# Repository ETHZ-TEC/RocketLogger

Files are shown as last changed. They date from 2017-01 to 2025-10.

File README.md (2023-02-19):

# RocketLogger

The RocketLogger is a mixed-signal data logger designed for measuring and validating energy
harvesting based devices. It features the portability required for measurements in the field,
accurate voltage and current measurements with a very high dynamic range, and simultaneously
sampled digital inputs to track the state of the measured device.

## Getting Started

To install a new RocketLogger system or the Python Support Library for measurement post processing,
refer to the [Installation](#installation) section. The latest RocketLogger releases are available
from <https://github.com/ETHZ-TEC/RocketLogger/releases>.

If you want to learn more about the details of the RocketLogger, head to the [Documentation](#documentation) section.

## Project Structure

The RocketLogger project consists of three parts:
* [RocketLogger Cape](hardware), an analog current and voltage measurement front-end designed as
  an extension board, a so-called *Cape*, for the [BeagleBone Green](https://beagleboard.org/green/),
* [RocketLogger Software Stack](software) that provides all management functionality for data
  logging, including low level C API, a command line utility, and an easy-to-use web interface,
* [RocketLogger Scripts](script) to import and process RocketLogger Data
  (RLD) files and to generate the calibration data files.

## Installation

The [RocketLogger releases](https://github.com/ETHZ-TEC/RocketLogger/releases) are accompanied by
a pre-built RocketLogger flasher image that allows installation of ready-to-use software on a
RocketLogger device:

1. Flash the RocketLogger flasher image `rocketlogger-flasher-vX.X.X.img.xz` (where `X.X.X` is the targeted release) onto an SD card
   using the `software/system/flash_image.sh` script.
2. Insert the SD card into the RocketLogger and wait for the installation to complete and the
   RocketLogger to power off.
3. Remove the SD card, power on the RocketLogger again, and start your first measurements.

For more details on the installation process and alterative deployment options, refer to the [RocketLogger Installation](https://github.com/ETHZ-TEC/RocketLogger/wiki/software) wiki page.

The Python support library is available from the [Python Package Index](https://pypi.org) and
is installed using pip:
```bash
python -m pip install rocketlogger
```

For the manual installation of individual software components, see the respective README files:
* [RocketLogger software](software/rocketlogger/README.md#installation)
* [Node.js web interface](software/node_server/README.md#installation)
* [Base operating system](software/system/README.md#installation)
* [Python support library](script/python/README.md#installation)

## Documentation

The documentation for the RocketLogger is found in the wiki pages at
<https://github.com/ETHZ-TEC/RocketLogger/wiki>.

## Versioning

The RocketLogger project uses [semantic versioning](https://semver.org) for its releases.

## Dependencies

### Hardware Design

The hardware was designed using Altium Designer (version 16.1 was used for the PCB design).

More details regarding the hardware design can be found in the wiki at
[RocketLogger Hardware Design Data](https://github.com/ETHZ-TEC/RocketLogger/wiki/design-data).

### Software Stack

The RocketLogger software is based on the [Debian](https://www.debian.org) operating system for
the BeagleBone platform provided by [BeagleBoard.org](https://beagleboard.org).

To compile the RocketLogger software, the following system components are required (to be installed
using `apt-get`):

```bash
curl device-tree-compiler gcc g++ git make meson/buster-backports ninja-build/buster-backports ntp pkg-config ti-pru-cgt-installer libgpiod-dev libi2c-dev libncurses5-dev libzmq3-dev
```
with recent `meson` and `ninja` release from the Debian *buster-backports* repository.
In addition, the software relies on the following two software repositories for Linux device tree
headers and PRU user space driver:
* [bb.org Overlays](https://github.com/beagleboard/bb.org-overlays.git)
* [AM335x PRU Package](https://github.com/beagleboard/am335x_pru_package.git)

To deploy the optional Node.js web interface for remote control, the
following system packages are required:

```bash
g++ make nginx nodejs
```
with the Node.js LTS version 18 from the [NodeSource Node.js](https://github.com/nodesource/distributions#readme)
repository.

The cross compilation and operating system patching scripts in addition require a Docker
installation, more specifically [Docker Buildx](https://docs.docker.com/buildx/working-with-buildx/)
and privileged permissions for system patching.

## Project Contributors

The following list of people contributed in the development of the RocketLogger project:
Andres Gomez,
Dominic Bernath,
Lothar Thiele,
Lukas Sigrist,
Matthias Leubin,
Roman Lim,
Stefan Lippuner.

RocketLogger logo design by: Ivanna Gomez.

The RocketLogger project is currently maintained by: Lukas Sigrist.

## License

The RocketLogger Project is released under [3-clause BSD license](https://opensource.org/licenses/BSD-3-Clause).
For more details refer to the [LICENSE](LICENSE) file.

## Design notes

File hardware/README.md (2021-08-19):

# RocketLogger Hardware

The RocketLogger hardware consists the following parts:
* [Case](case) - Design files for the 3D printed RocketLogger case and acrylic cover
* [PCB Design](pcb) - RocketLogger PCB design data
* [Measurement Probes](probes) - RocketLogger probe specifications
* [Circuit Simulation](simulations) - Simulation data of different circuit parts of the RocketLogger

See also the documentation in the [RocketLogger Wiki](https://github.com/ETHZ-TEC/RocketLogger/wiki).

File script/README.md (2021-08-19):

# RocketLogger Scripts for Data Post-Processing

The RocketLogger scripts include the following parts:
* [MATLAB](matlab) - scripts to process RocketLogger data (`*.rld`) files using MATLAB [deprecated]
* [Python Support Library](python) - Python library to process RocketLogger data (`*.rld`) files, and perform and generate device calibration data

See also the documentation in the [RocketLogger Wiki](https://github.com/ETHZ-TEC/RocketLogger/wiki).

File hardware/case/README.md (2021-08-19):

# RocketLogger Case Design Files

## 3D Printed Case
The main 3D printer case was drawn with *Solidworks*: [rocket_case_v1.SLDPRT](rocket_case_v1.SLDPRT).

It was then exported as `.stl` and saved in the folder [`FILES_FOR_MANUFACTURING`](FILES_FOR_MANUFACTURING/).

## 3D Push Button Extender
The button extender is also a *Solidworks* object exported as `.stl` into the folder [`FILES_FOR_MANUFACTURING`](FILES_FOR_MANUFACTURING/).

## Cover Plate
The cover plate is drawn in *Inkscape* as a 2D graphics with different coloring for cut or engraved lines (RED=*cut*, BLACK=*engrave*).
This SVG file can be opened in *Inkscape* in the [PDZ machine room at ETH HG](https://pdz.ethz.ch/) for laser engraving and cutting.

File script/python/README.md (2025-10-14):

# RocketLogger Python Support Library

This package provides RocketLogger data file handling support, as well as
basic processing and plotting of the data. Further, it provides the necessary
support to generate calibration data from measurements.

**Dependencies**
* Python 3: version 3.6-3.14
* NumPy: version 1.13-2.3

**Optional dependencies**
* Matplotlib: for plotting data overview
* pandas: for pandas DataFrame export

**Compatibility**
* Data processing: supports all officially specified RLD file version (versions 2-4)
* Calibration: compatible with RocketLogger calibration file version 2

## Installation

The package is available from the [Python Package Index](https://pypi.org/project/rocketlogger/)
Install the package using pip:
```bash
python -m pip install rocketlogger
```

## Getting Started

### RocketLogger Data Processing

To import a RocketLogger data (`*.rld`) file, use the `RocketLoggerData` class:
```py
>>> from rocketlogger.data import RocketLoggerData
>>> rld = RocketLoggerData('data.rld')
```

To merge channels with auto-ranging, i.e. the current channels:
```py
>>> rld.merge_channels()
```

To get the loaded channel data (by name) and corresponding timestamps:
```py
>>> d = rld.get_data(['V1', 'I1'])
>>> t = rld.get_time()
```

For more details about the individual functions and their parameters, refer to
the documentation available at <https://github.com/ETHZ-TEC/RocketLogger/wiki/python>.

### RocketLogger Device Calibration

The `RocketLoggerCalibration` class from the `rocketlogger.calibration` module
provides the necessary support for generating RocketLogger device calibration.
See the [Calibration](https://github.com/ETHZ-TEC/RocketLogger/wiki/calibration) wiki section for more details on the calibration
procedure.

## Documentation

The documentation for the RocketLogger is found in the wiki pages at
<https://github.com/ETHZ-TEC/RocketLogger/wiki>.

## License

The RocketLogger Project is released under [3-clause BSD license](https://opensource.org/licenses/BSD-3-Clause).
For more details, refer the the [LICENSE](LICENSE) file.

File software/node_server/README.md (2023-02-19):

# RocketLogger Node.js Web Interface

## Features

The RocketLogger web interface features are summarized as follows:

* static source file serving
* dynamic site rendering using *nunjucks*
* RocketLogger CLI interface from web
* websockets for server side data streaming using *socket.io* and *zeromq*

## Installation

To install the webserver and its dependencies and to deploy it as system service,
use the provided installer script:
```bash
sudo ./install.sh
```
This script takes care of installing and configuring the additional system
and *npm* package dependencies listed under
[Dependencies](#dependencies-and-requirements).

To install the node.js server standalone in the source directory, use:
```
npm install .
```
When choosing this method, system package dependencies need to be installed
and configured manually.

## Dependencies and Requirements

* Server: Node.js v18 or later, *NGINX* for reverse proxy
* Client: reasonably recent web browser supporting *ECMAScript* 6

### Node.js server dependencies

* `express` - minimalist web framework
* `nunjucks` - Jinja2 inspired web template engine
* `socket.io` - websockets server side JavaScript library
* `zeromq` - ZeroMQ message queueing library
* `gulp` - file system listing
* `debug` - debugging output utility

### Browser client dependencies

* `bootstrap` - responsive, mobile-first front-end component library
* `plotly.js` - JavaScript plotting library
* `timesync` - client-server time synchronization library
* `socket.io-client` - websockets client side JavaScript library

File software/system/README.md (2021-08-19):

# RocketLogger Base System Setup

The RocketLogger system relies on Debian as a base operating system, with dedicated system
configuration and package installation. This software component provides the necessary
scripts to setup and configure the operating system.

## Installation
There are two alternative ways to setup the RocketLogger system:
1. remotely configuring the booted live system and install the software after a reboot (legacy
   installation to deploy system, requiring individual deployment)
2. patching the image locally with configuration and software and flash the ready-to-use image
   (pre-built image for mass deployment of many devices)

It is highly recommended to use the external SD card for configuration and measurement data
storage and boot from the eMMC. This provides more storage for data and prevents the system from getting unresponsive
due to running out of system disk space.

### Remote Setup

1. download the image using the `get_image.sh` script
2. insert the SD card into your computer and flash the downloaded image to it using
   `flash_image.sh <image.img.xz> <disk-device>`, where `<image.img.xz>` is the downloaded image
   file and `<disk-device>` the SD card device, typically `/dev/sdX` or `/dev/mmcblkX` (without
   any partition suffix!)
3. insert the SD card into the RocketLogger device and power it up
4. wait for the image to be copied to internal memory, i.e. until all LED are turned off again
5. remove the SD card and reboot the system by power cycling it
6. reboot and remotely run the setup using `remote_setup.sh <ip-addr> [<hostname>]`, where `<ip-addr>` is
   the network address under which the logger is reachable and `[<hostname>]` an optional hostname to
   configure during setup
7. optionally, but highly recommended, set up the external SD card as configuration and
   measurement data storage as described below
8. power up the RocketLogger and start your measurements

### Patch BeagleBone System Image

1. (skip this step when using a pre-built RocketLogger image) use the `patch_image.sh` script from
   the parent directory to download and patch the BeagleBone flasher image. This script requires a
   Docker Buildx setup as described under [dependencies](#dependencies).
2. flash the resulting `rocketlogger-*.img` file: insert the SD card into your computer and flash
   the `rocketlogger-*.img` image to it using `flash_image.sh rocketlogger-*.img <disk-device>`,
   where `<disk-device>` is the SD card device, typically `/dev/sdX` or `/dev/mmcblkX` (without any
   partition suffix!)
3. insert the SD card into the RocketLogger device and power it up
4. wait for the image to be copied to internal memory, i.e. until all LED are turned off again
5. remove the SD card and reboot the system
6. optionally, but highly recommended, set up the external SD card as configuration and
   measurement data storage as described below
7. power up the RocketLogger and start your measurements

### Set up External SD Card for Data and Configuration Storage

1. (re-)insert the SD card into your computer and prepare the RocketLogger SD card using
   `prepare_sdcard.sh <disk-device>`, where `<disk-device>` is the SD card device, typically
   `/dev/sdX` or `/dev/mmcblkX` (without any partition suffix!)
2. copy any existing configuration or calibration files into the `rocktlogger/config` folder
   on the newly set up SD card
3. Insert the SD card into the RocketLogger, reboot, and start your measurements

## Dependencies

The operation system is based on the minimal console images for the BeagleBone platform, provided
by [BeagleBoard.org](https://beagleboard.org). The latest official BeagleBone images are available
at <https://beagleboard.org/latest-images>.

The system installation scripts itself rely on Linux system utility binaries and partitioning and
filesystem tools that are typically included with any basic Linux based operating system.
Tools that might not come preinstalled with your favorite Linux operating system installation are:
`curl`, `dd`, `git`, `xz`.

### Docker Buildx for ARM System Image Patching

The local patching of a BeagleBone system image requires `Docker Buildx` and a system configured
to run privileged Docker containers. More information on the docker configuration is found at
[Docker Buildx](https://docs.docker.com/buildx/working-with-buildx/) and in the
[docker run reference](https://docs.docker.com/engine/reference/run/#runtime-privilege-and-linux-capabilities).

In a nutshell, Docker with Buildx and privileged support is installed as follows on a fresh
Ubuntu LTS 20.04 system (see the corresponding links for in-depth details):

1. install [Docker on Ubuntu](https://docs.docker.com/engine/install/ubuntu/):
   ```bash
   sudo apt-get install apt-transport-https ca-certificates curl gnupg lsb-release
   curl -fsSL https://download.docker.com/linux/ubuntu/gpg | sudo gpg --dearmor -o /usr/share/keyrings/docker-archive-keyring.gpg
   echo "deb [arch=amd64 signed-by=/usr/share/keyrings/docker-archive-keyring.gpg] https://download.docker.com/linux/ubuntu $(lsb_release -cs) stable" | sudo tee /etc/apt/sources.list.d/docker.list > /dev/null
   sudo apt-get update
   sudo apt-get install docker-ce docker-ce-cli containerd.io
   ```

2. add the user to the `docker` group to start Docker containers without root permissions [after the installation](https://docs.docker.com/engine/install/linux-postinstall/):
   ```bash
   sudo groupadd docker
   sudo usermod --append --groups docker ${USER}
   ```

Finally, reboot to apply the new user configurations.

Now, the Docker Buildx setup should be ready for cross-compilation and patching of an arm-v7 Debian
system image using the `patch_image.sh` script.

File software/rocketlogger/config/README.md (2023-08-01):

# RocketLogger System Configuration

This folder includes operating system and RocketLogger default configuration files
* uEnv configuration patch `uEnv.txt.patch` to deploy RocketLogger device tree overlay and activate PRU uio interface
* uio_pruss kernel module parameter configuration file `rocketlogger.conf`
* systemd service configuration for RocketLogger daemon `rocketlogger.service`
* design data based default calibration `calibration.dat`

## Documentation

### PRU Resources
* uEnv configuration to switch from rproc to uio PRU interface: <https://gist.github.com/jonlidgard/1d9e0e92b4f219f3f40edfed260b851e>

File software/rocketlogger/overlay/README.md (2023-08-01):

# RocketLogger Device Tree Overlay

This folder includes the device tree overlay source for the RocketLogger software.

## Documentation

### Linux Kernel v4.19 Documentation

#### Device Tree Documentation
* <https://github.com/torvalds/linux/blob/v4.19/Documentation/devicetree/usage-model.txt>
* <https://github.com/torvalds/linux/tree/v4.19/Documentation/devicetree/bindings>
* <https://github.com/torvalds/linux/blob/v4.19/Documentation/devicetree/bindings/pwm/pwm.txt>
* <https://github.com/torvalds/linux/blob/v4.19/Documentation/devicetree/bindings/pwm/pwm-tiehrpwm.txt>

#### PWM Documentation
* <https://github.com/torvalds/linux/blob/v4.19/Documentation/pwm.txt>

### PRU Resources
* switch from rproc to uio PRU interface: <https://gist.github.com/jonlidgard/1d9e0e92b4f219f3f40edfed260b851e>

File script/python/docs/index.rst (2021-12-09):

Welcome to the RocketLogger Python Support documentation!
=========================================================

.. toctree::
    :maxdepth: 2
    :titlesonly:
    :glob:
    :hidden:

    data
    calibration
    rocketlogger

The ``rocketlogger`` package provides support for handling RocketLogger data files and for
generation of RocketLogger device calibration file from measurements.

Features
--------

Python support for RocketLogger Data (``*.rld``) files by the :mod:`rocketlogger.data` module.
Supports any officially specified RocketLogger data file version (versions 2-4).

- Import
- Channel merging
- Data extraction
- Plotting of file data

Support for RocketLogger Device Calibration by the :mod:`rocketlogger.calibration` module.

- Generate new calibrations from measurements
- Read/write calibration files
- Validate the accuracy of new and existing calibrations

Installation
------------

Install the RocketLogger Python Support from the `Python Package Index <https://pypi.org/project/rocketlogger/>`_ using:

    ``pip install rocketlogger``

Testing
-------

The source installation comes with automated test cases and the relevant sample data.
For more details see the test documentation of :doc:`tests`.

Contribute
----------

- Source code:   https://github.com/ETHZ-TEC/RocketLogger
- Issue tracker: https://github.com/ETHZ-TEC/RocketLogger/issues
- Documentation: https://github.com/ETHZ-TEC/RocketLogger/wiki/python

License
-------

The project is licensed under the 3-Clause BSD License. See the package's ``LICENSE`` file for more details.

Indices and Tables
------------------

* :ref:`genindex`
* :ref:`modindex`
* :ref:`search`

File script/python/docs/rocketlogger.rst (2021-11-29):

Package Reference
=================

The Python support for RocketLogger is provided by the :mod:`rocketlogger` module.

Submodules
----------

.. toctree::
    :maxdepth: 2
    :titlesonly:

    rocketlogger.data
    rocketlogger.calibration
    tests

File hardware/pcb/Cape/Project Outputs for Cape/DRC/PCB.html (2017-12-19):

Altium

# Design Rule Verification Report

Date: | | 08.05.2017
Time: | | 17:00:02
Elapsed Time: | | 00:00:15
Filename: | | C:\Users\user\Documents\RocketLogger\rocketlogger\hardware\pcb\Cape\PCB.PcbDoc

Warnings: | | 0
Rule Violations: | | 12

## Summary

Warnings | Count
Total | 0

Rule Violations | Count
Assembly Testpoint Usage (Valid =Don't care, Allow multiple per net=No) (All) | 0
Room RangeValidStretching (Bounding Region = (102.6mm, 113.4mm, 117.5mm, 125.1mm) (InComponentClass('RangeValidStretching')) | 0
Room ADC 1 (Bounding Region = (97.1mm, 103.5mm, 118.4mm, 124.6mm) (InComponentClass('ADC 1')) | 0
Room Digital Channels 3 & 4 (Bounding Region = (99.1mm, 100.7mm, 105.5mm, 107mm) (Disabled)(InComponentClass('Digital Channels 3 & 4')) | 0
Room Digital Channels 1 & 2 (Bounding Region = (100.4mm, 107.1mm, 106.8mm, 113.4mm) (Disabled)(InComponentClass('Digital Channels 1 & 2')) | 0
Room Digital Channels 5 & 6 (Bounding Region = (99.9mm, 92.85mm, 106.3mm, 99.15mm) (Disabled)(InComponentClass('Digital Channels 5 & 6')) | 0
Room Current Channel 2 (Bounding Region = (121.1mm, 82.7mm, 176.7mm, 103.9mm) (InComponentClass('Current Channel 2')) | 0
Board Clearance Constraint (Gap=0mm) (All) | 4
Room top (Bounding Region = (129.1mm, 125.1mm, 131mm, 127.6mm) (Disabled)(InComponentClass('top')) | 0
Modified Polygon (Allow modified: No), (Allow shelved: No) | 0
Net Antennae (Tolerance=0mm) (All) | 8
Minimum Solder Mask Sliver (Gap=0.1mm) (All),(All) | 0
Hole To Hole Clearance (Gap=0.254mm) (All),(All) | 0
Assembly Testpoint Style (Under Component=Yes) (All) | 0
Assembly Testpoint Usage (Valid =One Required, Allow multiple per net=Yes) (InNetClass('AssemblyTP')) | 0
Height Constraint (Min=0mm) (Max=30mm) (Prefered=12.7mm) (All) | 0
Hole Size Constraint (Min=0.025mm) (Max=2.54mm) (Disabled)(All) | 0
Hole Size Constraint (Min=0.025mm) (Max=2.54mm) (Disabled)(All) | 0
Hole Size Constraint (Min=0.2mm) (Max=6mm) (All) | 0
Component Clearance Constraint ( Horizontal Gap = 0.1mm, Vertical Gap = 0.254mm ) (Not InComponent('S1')),(Not InComponent('S1')) | 0
Un-Routed Net Constraint ( (All) ) | 0
Short-Circuit Constraint (Allowed=No) (All),(All) | 0
Power Plane Connect Rule(Relief Connect )(Expansion=0.4mm) (Conductor Width=0.15mm) (Air Gap=0.15mm) (Entries=4) (InPadClass('All Pads')) | 0
Width Constraint (Min=0.125mm) (Max=10mm) (Preferred=0.2mm) (All) | 0
Clearance Constraint (Gap=0.125mm) (All),(All) | 0
Room ADC 2 (Bounding Region = (97.1mm, 81.9mm, 118.4mm, 103mm) (InComponentClass('ADC 2')) | 0
Room Cape (Bounding Region = (81.9mm, 114.4mm, 96.6mm, 130.9mm) (Disabled)(InComponentClass('Cape')) | 0
Room PSU (Bounding Region = (76.3mm, 76.2mm, 95.8mm, 97.4mm) (Disabled)(InComponentClass('PSU')) | 0
Width Constraint (Min=0.125mm) (Max=2mm) (Preferred=0.35mm) (InNetClass('Power')) | 0
Room Current Channel 1 (Bounding Region = (121mm, 102.9mm, 177.5mm, 122.6mm) (InComponentClass('Current Channel 1')) | 0
Room Voltage Channels 1 & 2 (Bounding Region = (145.846mm, 113.946mm, 176.629mm, 137.743mm) (InComponentClass('Voltage Channels 1 & 2')) | 0
Room Voltage Channels 3 & 4 (Bounding Region = (144.596mm, 69.264mm, 176.629mm, 92.804mm) (InComponentClass('Voltage Channels 3 & 4')) | 0
Power Plane Connect Rule(Direct Connect )(Expansion=0.4mm) (Conductor Width=0.15mm) (Air Gap=0.15mm) (Entries=4) (IsVia) | 0
Total | 12

Board Clearance Constraint (Gap=0mm) (All)

Board Outline Clearance(Outline Edge): (0.232mm < 0.3mm) Between Text "E" (93.7mm,129.875mm) on Top Overlay And Board Edge

Board Outline Clearance(Outline Edge): (0.232mm < 0.3mm) Between Text "S" (92.3mm,129.875mm) on Top Overlay And Board Edge

Board Outline Clearance(Outline Edge): (0.23mm < 0.3mm) Between Text "46" (153.4mm,129.9mm) on Top Overlay And Board Edge

Board Outline Clearance(Outline Edge): (0.27mm < 0.3mm) Between Text "TP412" (92.1mm,76.6mm) on Bottom Overlay And Board Edge

Back to top

Net Antennae (Tolerance=0mm) (All)

Net Antennae: Track (153.65mm,118.75mm)(153.9mm,118.75mm) on Component Side

Net Antennae: Track (153.35mm,89.502mm)(153.35mm,89.834mm) on Component Side

Net Antennae: Track (153.388mm,88.518mm)(153.56mm,88.691mm) on Component Side

Net Antennae: Track (155.2mm,89.3mm)(155.769mm,88.731mm) on Component Side

Net Antennae: Track (155.488mm,86.338mm)(155.488mm,87.909mm) on Component Side

Net Antennae: Track (156.25mm,118.225mm)(156.725mm,118.225mm) on Component Side

Net Antennae: Track (153.4mm,118.4mm)(155.4mm,118.4mm) on GND

Net Antennae: Track (153.7mm,89.7mm)(155.1mm,89.7mm) on GND

Back to top

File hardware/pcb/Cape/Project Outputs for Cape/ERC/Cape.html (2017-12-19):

Altium

# Electrical Rule Check Report

Date: | | 08.05.2017
Time: | | 16:59:17
Filename: | | C:\Users\user\Documents\RocketLogger\rocketlogger\hardware\pcb\Cape\Project Outputs for Cape\ERC\Cape.html

Class | Document | Message

Successful Compile; No Violations Found.

Back to top

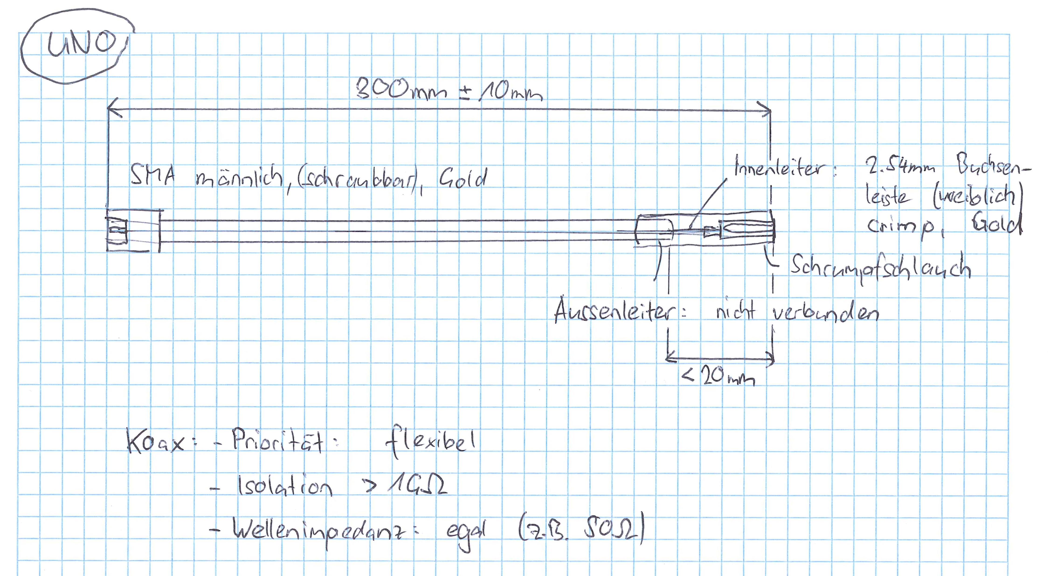
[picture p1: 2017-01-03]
hardware/probes/drawing_voltage.jpg

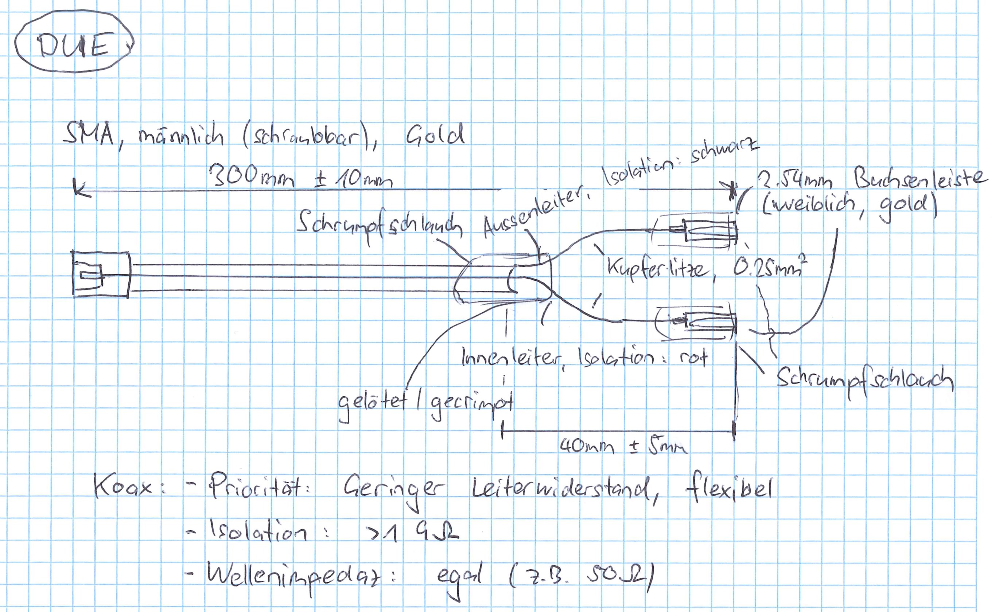
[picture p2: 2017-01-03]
hardware/probes/drawing_current.jpg

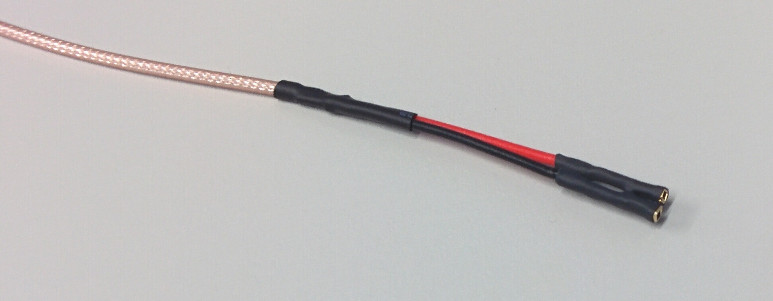
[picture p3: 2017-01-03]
hardware/probes/photo_current.jpg

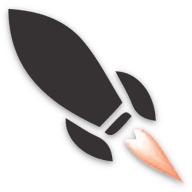
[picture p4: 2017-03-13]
software/node_server/static/android-chrome-192x192.png

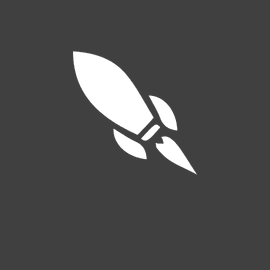
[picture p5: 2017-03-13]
software/node_server/static/mstile-150x150.png

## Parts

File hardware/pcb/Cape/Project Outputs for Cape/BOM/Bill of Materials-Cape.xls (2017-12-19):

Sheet: BOM Report
Bill of Materials |  |  | Bill of Materials For Project [Cape.PrjPcb] (PCB Document : PCB.PcbDoc)
Source Data From: |  | Cape.PrjPcb
Project: |  | Cape.PrjPcb
Variant: |  | None
Creation Date: | 08.05.2017 | 16:59:52
Print Date: | 2017-05-08 | 42863.70835
Production Quantity: | 1
Currency | <none>
Footprint | Comment | LibRef | Designator | Description | Quantity | Supplier 1 | Supplier Part Number 1 | Supplier Unit Price 1 | Supplier Order Qty 1 | Supplier Subtotal 1 | Manufacturer 1 | Manufacturer Part Number 1
 | TSW-123-07-L-D (BOM) | TSW-123-07-L-D (BOM) | P8, P9 | Conn Unshrouded Header HDR 46 POS 2.54mm Solder ST Thru-Hole | 2 | Digi-Key | SAM1030-23-ND | 3.94 | 2 | $7.88 | Samtec Inc. | TSW-123-07-L-D
TSW-107-07-L-S | TSW-107-07-L-S | TSW-107-07-L-S | J1 | Conn Unshrouded Header HDR 7 POS 2.54mm Solder ST Thru-Hole | 1 | Digi-Key | SAM1031-07-ND | 1.01 | 1 | $1.01 | Samtec Inc. | TSW-107-07-L-S
RESC0402(1005)_L | 10K, 25ppm/°C | CMP-1591-00004-1 | R305_1, R305_2, R306_1, R306_2, R504_1, R504_2, R505_1, R505_2 | 10K, 25ppm/°C 0402 (1005 Metric) Chip Resistor | 8 | Digi-Key | RR05P10.0KDDKR-ND | 0.1 | 8 | $0.80 | Susumu | RR0510P-103-D
RESC0402(1005)_L | 133R, 25ppm/°C | CMP-1591-00004-1 | R301_1, R301_2 | 133R, 25ppm/°C, 0402 (1005 Metric) Chip Resistor | 2 | Digi-Key | A102612DKR-ND | 0.6 | 2 | $1.20 | TE Connectivity Passive Product | CPF0402B133RE1
RESC0402(1005)_L | 3K9, 25ppm/°C | CMP-1591-00004-1 | R506_1, R506_2, R507_1, R507_2 | 3K9, 25ppm/°C, 0402 (1005 Metric) Chip Resistor | 4 | Digi-Key | RR05P3.9KDCT-ND | 0.1 | 4 | $0.40 | Susumu | RR0510P-392-D
RESC0402(1005)_L | 680R, 25ppm/°C | CMP-1591-00004-1 | R302_1, R302_2 | 680R, 25ppm/°C 0402 (1005 Metric) Chip Resistor | 2 | Digi-Key | RR05P680DCT-ND | 0.1 | 2 | $0.20 | Susumu | RR0510P-681-D
CAPC0402(1005)60_L | 33nF | CMP-1590-00004-1 | C312_1, C312_2 | CAP 33nF 16V ±5%, 0402 (1005 Metric) Chip Capacitor | 2 | Digi-Key | 399-8964-6-ND | 0.47 | 2 | $0.94 | KEMET | C0402C333J4RACTU
CAPC1210(3225)200_L | 100uF | CMP-1590-00002-1 | C435, C436 | CAP 100uF 10V ±20% 1210 (3225 Metric) SMD | 2 | Digi-Key | 490-9969-6-ND | 1.03 | 2 | $2.06 | Murata Electronics North America | GRM32ER61A107ME20L
0603_A | Blue, 2.6V @ 2mA | CMP-1426-00003-1 | LED200, LED201 | SMD mono-color Chip LED, WL-SMCW, Blue | 2 | Newark | 95W3793 | 0.24 | 2 | $0.48 | Wuerth Elektronik | 150060BS75000
0603_A | Red, 1.6V @ 2mA | CMP-1426-00001-1 | LED202 | SMD mono-color Chip LED, WL-SMCW, Red | 1 | Newark | 95W3795 | 0.22 | 1 | $0.22 | Wuerth Elektronik | 150060RS75000
INF-PG-SOT-323_L | BSS214NW | CMP-1149-00041-1 | Q301_1, Q301_2 | N-Channel OptiMOS 2 Small-Signal-Transistor, 20 V VDS, 1.5 A ID, -55 to 150 degC, PG-SOT-323, Reel, Green | 2 |  |  | 0 | 2 | $0.00 | INFINEON | BSS214NW
CAPC1210(3225)280_L | 47uF | CMP-1038-02296-1 | C404, C414, C415 | CAP 47uF 16V ±20% 1210 (3225 Metric) Thickness 2.8mm SMD | 3 | Newark | 60M1034 |  | 3 |  | KEMET | C1210C476M4PACTU
CAPC0805(2012)145_L | 22uF | CMP-1036-04938-1 | C128_1, C128_2 | CAP 22uF 6.3V ±10% 0805 (2012 Metric) Thickness 1.45mm SMD | 2 | Newark | 87R3911 |  | 2 |  | Yageo | C2012X5R0J226K/1.25
CAPC0603(1608)100_L | 10uF | CMP-1035-02800-1 | C123_1, C123_2, C308_1, C308_2, C309_1, C309_2, C317_1, C317_2, C318_1, C318_2, C319_1, C319_2, C402, C406, C417, C418, C419, C420, C421, C422, C426, C428, C431, C432, C433, C434, C437 | CAP 10uF 10V ±20% 0603 (1608 Metric) Thickness 1mm SMD | 27 | Newark | 48T2910 | 0.2 | 27 | $5.40 | Yageo | C1608X5R1A106M
CAPC0402(1005)60_L | 1uF | CMP-1034-02120-1 | C100_1, C100_2, C101_1, C101_2, C102_1, C102_2, C103_1, C103_2, C104_1, C104_2, C105_1, C105_2, C106_1, C106_2, C107_1, C107_2, C124_1, C124_2, C125_1, C125_2, C127_1, C127_2, C409 | CAP 1uF 16V ±20% 0402 (1005 Metric) Thickness 0.6mm SMD | 23 | Newark | 87R3280 |  | 23 |  | Yageo | C1005X5R1C105M
CAPC0402(1005)60_L | 220nF | CMP-1034-02088-1 | C408 | CAP 220nF 10V -20% to +80% 0402 (1005 Metric) Thickness 0.6mm SMD | 1 | Newark | 65R7759 |  | 1 |  | Yageo | CC0402ZRY5V6BB224
CAPC0402(1005)60_L | 100nF | CMP-1034-02071-1 | C122_1, C122_2, C126_1, C126_2, C200, C201, C300_1, C300_2, C301_1, C301_2, C302_1, C302_2, C303_1, C303_2, C304_1, C304_2, C305_1, C305_2, C306_1, C306_2, C307_1, C307_2, C315_1, C315_2, C316_1, C316_2, C320_1, C320_2, C322_1, C322_2, C400, C401, C403, C405, C407, C416, C425, C427, C500_1, C500_2, C501_1, C501_2, C600_1, C600_2, C600_3, C700, C701 | CAP 100nF 16V -20% to +80% 0402 (1005 Metric) Thickness 0.6mm SMD | 47 | Newark | 16J0455 |  | 47 |  | Vishay | VJ0402V104ZXJCW1BC
CAPC0402(1005)60_L | 10nF | CMP-1034-01879-1 | C323_1, C323_2, C325_1, C325_2, C410, C423, C424, C429, C430 | CAP 10nF 25V ±5% 0402 (1005 Metric) Thickness 0.6mm SMD | 9 | Newark | 07J4433 |  | 9 |  | KEMET | C0402C103J3RACTU
CAPC0402(1005)60_L | 4.7nF | CMP-1034-01817-1 | C411 | CAP 4.7nF 50V ±20% 0402 (1005 Metric) Thickness 0.6mm SMD | 1 |  |  | 0 | 1 | $0.00 | Vishay | VJ0402Y472MXAAC
CAPC0402(1005)60_L | 2.2nF | CMP-1034-01741-1 | C310_1, C310_2 | CAP 2.2nF 50V ±5% 0402 (1005 Metric) Thickness 0.6mm SMD | 2 | Newark | 07X0701 |  | 2 |  | KEMET | C0402C222J5RACTU
CAPC0402(1005)60_L | 1nF | CMP-1034-01626-1 | C108_1, C108_2, C109_1, C109_2, C110_1, C110_2, C111_1, C111_2, C113_1, C113_2, C114_1, C114_2, C115_1, C115_2, C116_1, C116_2, C117_1, C117_2, C118_1, C118_2, C120_1, C120_2, C121_1, C121_2, C321_1, C321_2, C324_1, C324_2 | CAP 1nF 50V ±5% 0402 (1005 Metric) Thickness 0.6mm SMD | 28 | Newark | 07X0679 |  | 28 |  | KEMET | C0402C102J5RACTU
CAPC0402(1005)60_L | 470pF | CMP-1034-01500-1 | C311_1, C311_2 | CAP 470pF 50V ±5% 0402 (1005 Metric) Thickness 0.6mm SMD | 2 | Newark | 07X0719 |  | 2 |  | KEMET | C0402C471J5RACTU
CAPC0402(1005)60_L | 120pF | CMP-1034-01275-1 | C412 | CAP 120pF 50V ±5% 0402 (1005 Metric) Thickness 0.6mm SMD | 1 |  |  | 0 | 1 | $0.00 | Vishay | VJ0402Y121JXAAC
CAPC0402(1005)60_L | 56pF | CMP-1034-01132-1 | C413 | CAP 56pF 50V ±5% 0402 (1005 Metric) Thickness 0.6mm SMD | 1 | Newark | 01J3929 |  | 1 |  | KEMET | C0402C560J5GACTU
CAPC0402(1005)60_L | 10pF | CMP-1034-00724-1 | C313_1, C313_2, C314_1, C314_2 | CAP 10pF 50V ±5% 0402 (1005 Metric) Thickness 0.6mm SMD | 4 | Newark | 03C3037 | 0.12 | 4 | $0.48 | KEMET | C0402C100J5GACTU
RESC0402(1005)_L | 205K | CMP-1011-00769-1 | R601_1, R601_2, R601_3, R603_1, R603_2, R603_3 | 205K 0.063W 1% 0402 (1005 Metric) SMD | 6 | Newark | 07J7643 |  | 6 |  | Vishay | CRCW0402205KFKTD
RESC0402(1005)_L | 115K | CMP-1011-00742-1 | R403, R405 | 115K 0.063W 1% 0402 (1005 Metric) SMD | 2 | Newark | 24W1943 |  | 2 |  | Vishay | CRCW0402115KFKED
RESC0402(1005)_L | 102K | CMP-1011-00737-1 | R413 | 102K 0.063W 1% 0402 (1005 Metric) SMD | 1 | Newark | 07J7504 |  | 1 |  | Vishay | CRCW0402102KFKTD
RESC0402(1005)_L | 100K | CMP-1011-00736-1 | R203, R204, R209, R315_1, R315_2, R316_1, R316_2, R320_1, R320_2, R600_1, R600_2, R600_3, R602_1, R602_2, R602_3, R700, R701, R704, R705 | 100K 0.063W 1% 0402 (1005 Metric) SMD | 19 | Newark | 07J7499 |  | 19 |  | Vishay | CRCW0402100KFKTD
RESC0402(1005)_L | 60K4 | CMP-1011-00711-1 | R312_1, R312_2 | 60K4 0.063W 1% 0402 (1005 Metric) SMD | 2 | Newark | 07J7869 | 0 | 2 | $0.00 | Vishay | CRCW040260K4FKTD
RESC0402(1005)_L | 51K1 | CMP-1011-00704-1 | R309_1, R309_2 | 51K1 0.063W 1% 0402 (1005 Metric) SMD | 2 | Newark | 07J7834 |  | 2 |  | Vishay | CRCW040251K1FKTD
RESC0402(1005)_L | 41K2 | CMP-1011-00692-1 | R412 | 41K2 0.063W 1% 0402 (1005 Metric) SMD | 1 | Newark | 07J7788 |  | 1 |  | Vishay | CRCW040241K2FKTD
RESC0402(1005)_L | 27K | CMP-1011-00670-1 | R415 | 27K 0.063W 1% 0402 (1005 Metric) SMD | 1 | Newark | 24W2143 |  | 1 |  | Vishay | CRCW040227K0FKED
RESC0402(1005)_L | 24K9 | CMP-1011-00666-1 | R406, R414 | 24K9 0.063W 1% 0402 (1005 Metric) SMD | 2 | Newark | 07J7682 | 0 | 2 | $0.00 | Vishay | CRCW040224K9FKTD
RESC0402(1005)_L | 20K5 | CMP-1011-00656-1 | R402 | 20K5 0.063W 1% 0402 (1005 Metric) SMD | 1 | Newark | 07J7642 |  | 1 |  | Vishay | CRCW040220K5FKTD
RESC0402(1005)_L | 12K4 | CMP-1011-00633-1 | R310_1, R310_2 | 12K4 0.063W 1% 0402 (1005 Metric) SMD | 2 | Newark | 07J7543 |  | 2 |  | Vishay | CRCW040212K4FKTD
RESC0402(1005)_L | 11K5 | CMP-1011-00629-1 | R311_1, R311_2 | 11K5 0.063W 1% 0402 (1005 Metric) SMD | 2 | Newark | 26W8979 |  | 2 |  | Vishay | CRCW040211K5FKED
RESC0402(1005)_L | 10K2 | CMP-1011-00624-1 | R411 | 10K2 0.063W 1% 0402 (1005 Metric) SMD | 1 | Newark | 07J7503 |  | 1 |  | Vishay | CRCW040210K2FKTD
RESC0402(1005)_L | 10K | CMP-1011-00623-1 | R114_1, R114_2, R115_1, R115_2, R116_1, R116_2, R303_1, R303_2, R304_1, R304_2, R313_1, R313_2, R318_1, R318_2, R319_1, R319_2, R404, R407, R409, R410, R500_1, R500_2, R501_1, R501_2, R502_1, R502_2, R503_1, R503_2, R604_1, R604_2, R604_3, R605_1, R605_2, R605_3 | 10K 0.063W 1% 0402 (1005 Metric) SMD | 34 | Newark | 07J7498 |  | 34 |  | Vishay | CRCW040210K0FKTD
RESC0402(1005)_L | 4K7 | CMP-1011-00586-1 | R100_1, R100_2, R101_1, R101_2, R103_1, R103_2, R104_1, R104_2, R105_1, R105_2, R106_1, R106_2, R107_1, R107_2, R108_1, R108_2, R110_1, R110_2, R111_1, R111_2, R112_1, R112_2, R113_1, R113_2 | 4K7 0.063W 1% 0402 (1005 Metric) SMD | 24 | Newark | 09J3779 | 0 | 24 | $0.00 | Vishay | CRCW04024K70FKTD
RESC0402(1005)_L | 3K9 | CMP-1011-00576-1 | R408 | 3K9 0.063W 1% 0402 (1005 Metric) SMD | 1 | Newark | 24W2177 |  | 1 |  | Vishay | CRCW04023K90FKED
RESC0402(1005)_L | 1K | CMP-1011-00510-1 | R200, R206, R314_1, R314_2, R416 | 1K 0.063W 1% 0402 (1005 Metric) SMD | 5 | Newark | 01C8605 | 0.01 | 5 | $0.05 | Vishay | CRCW04021K00FKTD
RESC0402(1005)_L | 100R | CMP-1011-00397-1 | R400 | 100R 0.063W 1% 0402 (1005 Metric) SMD | 1 | Newark | 07J7496 |  | 1 |  | Vishay | CRCW0402100RFKTD
RESC0402(1005)_L | 75R | CMP-1011-00383-1 | R307_1, R307_2 | 75R 0.063W 1% 0402 (1005 Metric) SMD | 2 | Newark | 07J7911 | 0 | 2 | $0.00 | Vishay | CRCW040275R0FKTD
RESC0402(1005)_L | 15R | CMP-1011-00302-1 | R321_1, R321_2, R322_1, R322_2 | 15R 0.063W 1% 0402 (1005 Metric) SMD | 4 | Newark | 07J7579 |  | 4 |  | Vishay | CRCW040215R0FKTD
RESC0402(1005)_L | 200K | CMP-1011-00129-1 | R702, R703 | 200K 0.063W 5% 0402 (1005 Metric) SMD | 2 | Newark | 43C3657 |  | 2 |  | Vishay | CRCW0402200KJNED
RESC0402(1005)_L | 5K6 | CMP-1011-00092-1 | R201, R202 | 5K6 0.063W 5% 0402 (1005 Metric) SMD | 2 | Newark | 19K8687 |  | 2 |  | Vishay | CRCW04025K60JNED
RESC0402(1005)_L | 820R | CMP-1011-00072-1 | R208 | 820R 0.063W 5% 0402 (1005 Metric) SMD | 1 | Newark | 43C4000 | 0 | 1 | $0.00 | Vishay | CRCW0402820RJNED
RESC0402(1005)_L | 330R | CMP-1011-00062-1 | R207 | 330R 0.063W 5% 0402 (1005 Metric) SMD | 1 | Newark | 19K8698 |  | 1 |  | Vishay | CRCW0402330RJNED
RESC0402(1005)_L | 12R | CMP-1011-00001-1 | R308_1, R308_2 | 12R 0.063W 1% 0402 (1005 Metric) SMD | 2 | Digi-Key | YAG2968DKR-ND | 0.1 | 2 | $0.20 | Yageo | RC0402FR-0712RL
DCU0008A_L | SN74AUP2G32DCUR | CMP-0859-00721-3 | U701 | Low-Power Dual 2-Input Positive-OR Gate, DCU0008A, LARGE T&R | 1 |  |  | 0 | 1 | $0.00 | Burr-Brown | SN74AUP2G32DCUR
DCK0006A_L | SN74LVC2G14DCKR | CMP-0859-00454-3 | U306_1, U306_2 | Dual Schmitt-Trigger Inverter, DCK0006A, LARGE T&R | 2 | Newark | 28X3890 |  | 2 |  | Burr-Brown | SN74LVC2G14DCKR
DCK0005A_L | SN74AHCT1G00DCKR | CMP-0859-00300-3 | U307_1, U307_2 | Single 2-Input Positive-NAND Gate, DCK0005A, LARGE T&R | 2 |  |  | 0 | 2 | $0.00 | Burr-Brown | SN74AHCT1G00DCKR
DBV0005A_L | LP2985-25DBVR | CMP-0758-00027-2 | U405 | Single Output Low Noise LDO, 150 mA, Fixed 2.5 V Output, 1.5% Tolerance, 2.2 to 16 V Input, Low IQ, 5-Pin SOT-23 (DBV), -40 to 125 degC, Green (RoHS & no Sb/Br), Tape and Reel | 1 | Newark | 14M2037 |  | 1 |  | Burr-Brown | LP2985-25DBVR
PW0016A_L | CD4503BPW | CMP-0440-01132-3 | U201 | CMOS Hex Non-Inverting Buffer with 3-State Outputs, PW0016A, TUBE | 1 |  |  | 0 | 1 | $0.00 | Burr-Brown | CD4503BPW
TI-DBV5_L | TPS72325DBVTG4 | CMP-0394-00283-1 | U408 | Single Output High PSRR LDO, 200 mA, Fixed -2.5 V Output, -10 to -2.7 V Input, 5-pin SOT-23 (DBV), -40 to 125 degC, Green (RoHS & no Sb/Br) | 1 | Newark | 54K1783 |  | 1 |  | Burr-Brown | TPS72325DBVTG4
SOT-23-TT3_N | SI2323DS-T1-GE3 | CMP-00292-1 | Q400 | MOSFET P-CH 20V 3.7A SOT23-3 | 1 |  |  | 0 | 1 | $0.00 | Unsupported client version. New PartCatalog supported starting from version 17.0
 | BMI-S-208-C | CMP-00232-1 | M1 | Board Mount EMI Enclosures RF Absorber CRS Tin SMD | 1 |  |  | 0 | 1 | $0.00 | Unsupported client version. New PartCatalog supported starting from version 17.0
132322 | CON-SMA-EDGE-S | CMP-00231-1 | J300_1, J300_2, J500_1, J500_2, J501_1, J501_2 | SMA FEMALE PCB EDGE MOUNT | 6 |  |  | 0 | 6 | $0.00 | Unsupported client version. New PartCatalog supported starting from version 17.0
KRM 2 Series | KMR231NG LFS | CMP-00230-1 | SW201 | SWITCH TACTILE SPST-NO 0.05A 32V | 1 |  |  | 0 | 1 | $0.00 | Unsupported client version. New PartCatalog supported starting from version 17.0
INDC0603(1608)_L | 1.5uH | CMP-00229-1 | L300_1, L300_2, L403, L404, L405, L406, L407, L408 | FIXED IND 1.5UH 50MA 700 MOHM | 8 |  |  | 0 | 8 | $0.00 | Unsupported client version. New PartCatalog supported starting from version 17.0
ACH32C | ACH32C-470-T001 | CMP-00228-1 | U300_1, U300_2 | LC (T-Type) EMI Filter 3rd Order Low Pass 1 Channel C = 47pF 6A 1206 (3216 Metric), 3 PC Pad | 2 |  |  | 0 | 2 | $0.00 | Unsupported client version. New PartCatalog supported starting from version 17.0
43W | 43WR500KLFTR | CMP-00227-2 | R401 | TRIMMER 500K OHM 0.125W SMD | 1 |  |  | 0 | 1 | $0.00 | Unsupported client version. New PartCatalog supported starting from version 17.0
SOT89_L | AP2204RA-5.0TRG1 | CMP-00226-1 | U406 | IC REG LDO Linear Voltage Regulator Positive Fixed 1 Output 5V 150mA SOT-89-3 | 1 |  |  | 0 | 1 | $0.00 | Unsupported client version. New PartCatalog supported starting from version 17.0
TSSOP-16_L | CD4043BPWR | CMP-00223-2 | U700 | IC NOR R/S LTCH 3ST QUAD 16TSSOP | 1 |  |  | 0 | 1 | $0.00 | Unsupported client version. New PartCatalog supported starting from version 17.0
PowerPAK_SO-8_V | CSD17527Q5A | CMP-00221-1 | Q300_1, Q300_2 | MOSFET N-CH 30V 65A 8SON | 2 |  |  | 0 | 2 | $0.00 | Unsupported client version. New PartCatalog supported starting from version 17.0
Z5+1_L | MIC5270-5.0YM5-TR | CMP-00219-1 | U407 | IC REG LDO Linear Voltage Regulator Negative Fixed 1 Output -5V 100mA SOT-23-5 | 1 |  |  | 0 | 1 | $0.00 | Unsupported client version. New PartCatalog supported starting from version 17.0
416131160802 | 218-2LPST | CMP-00125-1 | SW200 | Switch DIP ON OFF SPST 2 Recessed Slide 0.025A 24VDC Gull Wing 1.27mm SMD | 1 |  |  | 0 | 1 | $0.00 | Unsupported client version. New PartCatalog supported starting from version 17.0
BMI-S-208-F | BMI-S-208-F | CMP-00123-4 | S1 | EMI Connector Gaskets & Grounding Pads BLS,2PSH,FRM,SnSat .276x1.559x1.559in | 1 |  |  | 0 | 1 | $0.00 | Unsupported client version. New PartCatalog supported starting from version 17.0
ADI-RM-8_L | AD8421ARMZ | CMP-00122-1 | U304_1, U304_2 | Instrument Amplifier, 1, 60 V, 35 V/ s, 10 MHz, 5V to 36V, MSOP | 2 |  |  | 0 | 2 | $0.00 | Unsupported client version. New PartCatalog supported starting from version 17.0
43W | 43WR10KLFTR | CMP-00121-2 | R317_1, R317_2 | TRIMMER 10K OHM 0.125W SMD | 2 |  |  | 0 | 2 | $0.00 | Unsupported client version. New PartCatalog supported starting from version 17.0
DIOD-SOD323-2_V | SD103CWS-7-F | CMP-00120-1 | D400, D401 | DIODE SCHOTTKY 20V 350MA SOD323 | 2 |  |  | 0 | 2 | $0.00 | Unsupported client version. New PartCatalog supported starting from version 17.0
INDC2520X10L | 4.7uH | CMP-00119-1 | L400, L401, L402 | FIXED IND 4.7UH 1A 110 MOHM SMD | 3 |  |  | 0 | 3 | $0.00 | Unsupported client version. New PartCatalog supported starting from version 17.0
TI-DRL5_L | TCR2EE12,LM(CT | CMP-00117-2 | U402 | IC REG LDO 1.2V 0.2A ESV | 1 |  |  | 0 | 1 | $0.00 | Unsupported client version. New PartCatalog supported starting from version 17.0
DRB8-1750X1500TP | TPS7A4901DRBR | CMP-00110-1 | U404 | LDO Voltage Regulators Vin 3V to 36V, 150mA, Ultra-Low Noise, High PSRR, Low-Dropout Linear Regulator 8-SON | 1 |  |  | 0 | 1 | $0.00 | Unsupported client version. New PartCatalog supported starting from version 17.0
DRB8-1750X1500TP | TPS7A3001DRBR | CMP-00109-1 | U403 | LDO Voltage Regulators Vin -3V to -36V, -200mA, Ultra-Low Noise, High PSRR, Low-Dropout Linear Regulator 8-SON | 1 |  |  | 0 | 1 | $0.00 | Unsupported client version. New PartCatalog supported starting from version 17.0
LT-UF-24_L | TPS65130RGER | CMP-00108-2 | U401 | Conv DC-DC Dual Inv/Step Up 2.7V to 5.5V 24-Pin VQFN EP | 1 |  |  | 0 | 1 | $0.00 | Unsupported client version. New PartCatalog supported starting from version 17.0
UDFN-MU8 | CAT24C256HU4IGT3 | CMP-00107-1 | U202 | IC EEPROM 256KBIT 400KHZ 8UDFN | 1 |  |  | 0 | 1 | $0.00 | Unsupported client version. New PartCatalog supported starting from version 17.0
TSSOP-ST14_L | OPA4192IPW | CMP-00106-1 | U500_1, U500_2 | Precision, Rail-to-Rail Input/Output, Low Offset Voltage, Low Input Bias Current Op Amp with e-trim | 2 |  |  | 0 | 2 | $0.00 | Unsupported client version. New PartCatalog supported starting from version 17.0
QFP50P1000X1000X120_HS-64L | ADS131E08SPAGR | CMP-00105-1 | U100_1, U100_2 | Analog to Digital Converters - ADC 8-Channel, 24-Bit, AFE | 2 |  |  | 0 | 2 | $0.00 | Unsupported client version. New PartCatalog supported starting from version 17.0
ADI-RM-8_L | ADA4522-2ARMZ | CMP-00103-1 | U302_1, U302_2, U303_1, U303_2, U400 | SP Amp Zero Drift Amplifier Dual R-R I/O ±27.5V/55V 8-Pin MSOP | 5 |  |  | 0 | 5 | $0.00 | Unsupported client version. New PartCatalog supported starting from version 17.0
RESC0603(1608)_L | 046702.5NR | CMP-00099-1 | F300_1, F300_2 | Fuse Chip Very Fast Acting 2.5A 32V SMD Solder Pad 0603 | 2 |  |  | 0 | 2 | $0.00 | Unsupported client version. New PartCatalog supported starting from version 17.0
WSK1206 | WSK1206R0500FEA | CMP-00094-1 | R300_1, R300_2 | RES SMD 0.05 OHM 1% 1/4W 1206 | 2 |  |  | 0 | 2 | $0.00 | Unsupported client version. New PartCatalog supported starting from version 17.0
Z5+1_L | RB496EATR | CMP-00093-1 | D300_1, D300_2 | DIODE ARRAY SCHOTTKY 20V TSMD5 | 2 |  |  | 0 | 2 | $0.00 | Unsupported client version. New PartCatalog supported starting from version 17.0
ADI-RM-8_L | TLV1702AIDGK | CMP-00089-1 | U305_1, U305_2 | Analog Comparators Dual 2.2V to 36V microPwr Comparator | 2 |  |  | 0 | 2 | $0.00 | Unsupported client version. New PartCatalog supported starting from version 17.0
M08A_L | AD8421BRZ | CMP-00086-1 | U301_1, U301_2 | Instrumentation Amplifier 3nV/Hz Low Power | 2 |  |  | 0 | 2 | $0.00 | Unsupported client version. New PartCatalog supported starting from version 17.0
DGK0008A_L | LMC6772AIMM/NOPB | CMP-0055-01401-3 | U600_1, U600_2, U600_3 | Dual Micro-Power Rail-to-Rail Input CMOS Comparator with Open Drain Output, 8-pin Mini SOIC, Pb-Free | 3 | Newark | 28X4270 |  | 3 |  | National Semiconductor | LMC6772AIMM/NOPB
 |  |  |  |  | 371 |  |  |  |  | $21.32
Approved |  | Notes

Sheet: Project Information
Project Full Path | C:\Users\user\Documents\RocketLogger\rocketlogger\hardware\pcb\Cape\Cape.PrjPcb
Project Filename | Cape.PrjPcb
Variant Name | None
Data-Source Filename | Cape.PrjPcb
Data-Source Full Path | C:\Users\user\Documents\RocketLogger\rocketlogger\hardware\pcb\Cape\Cape.PrjPcb
Title | Bill of Materials For Project [Cape.PrjPcb] (PCB Document : PCB.PcbDoc)
Total Quantity | 371
Report Time | 16:59:52
Report Date | 08.05.2017
Report Date & Tine | 08.05.2017 16:59:52
Output Name | Bill of Materials
Output Type | BOM_PartType
Output Generator Name | BOM
Output Generator Description | Bill of Materials

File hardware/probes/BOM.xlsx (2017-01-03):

Part | Manufacturer | MPN | Octopart Link | Notes
Buchsenkontakte | FCI | 47745-001LF | https://octopart.com/47745-001lf-fci-40487264
SMA Stecker | Amphenol Connex | 132114 | https://octopart.com/132114-amphenol+connex-39391640
Koaxialkabel | Molex / Temp-Flex | 086SC-2401 | https://octopart.com/086sc-2401-molex+%2F+temp-flex-38787187 | DigiKey: http://www.digikey.com/product-search/en?keywords=086sc-2401
Mini Hook Black | E-Z-Hook | XR25BLK | https://octopart.com/xr25blk-e-z-hook-19790456
Mini Hook Red | E-Z-Hook | XR25RED | https://octopart.com/xr25red-e-z-hook-19790462

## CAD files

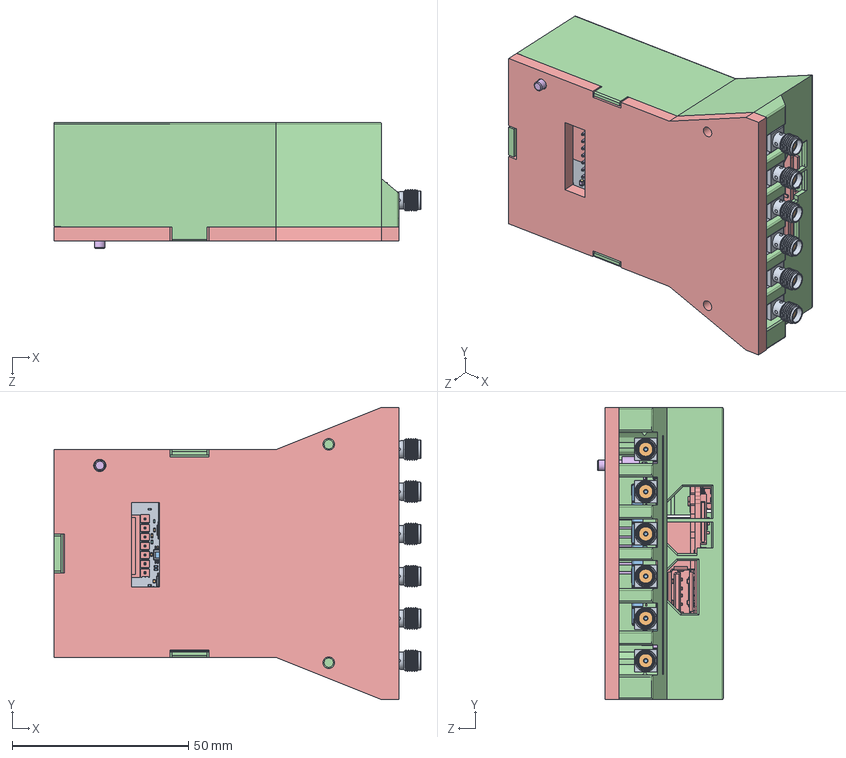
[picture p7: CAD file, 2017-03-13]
hardware/case/assembly_of_case_and_boards.SLDASM
104.2 x 83.0 x 35.8 mm
BoardPCB
Extruded x 104
Extruded_2 x 52
Extruded_3 x 8
Extruded_4 x 14
Extruded_5 x 17
Extruded_6 x 34
Extruded_7 x 2
Extruded_8
Extruded_9 x 121
Extruded_10 x 142
Extruded_11 x 9
_TSW-107-07-G-S_body
_T-1S6-07-TSW-1-07-7-S
Extruded_12 x 172
Extruded_13 x 86
housing x 3
cover x 3
base x 6
Polarity_Mark x 3
Extruded_14 x 10
Extruded_15 x 20
Extruded_16
Extruded_17 x 2
BODY_MUY08A x 3
LEAD_MUY08A x 24
EXP_PAD_MUY08A x 3
BODY_MTC16
LEAD_MTC16 x 16
DCU0008A
Extruded_18 x 3
Extruded_19 x 100
BD11ARJ09-STAKE x 6
NS11AAG70 x 6
CP11APC07 x 6
Extruded_20 x 2
User_Library-BEAGLEBONE_BLACK
Extruded_21 x 92
Extruded_22 x 92
Extruded_23
Extruded_24
Extruded_25 x 2
Extruded_26 x 4
Extruded_27
Extruded_28
Extruded_29
Extruded_30
Extruded_31 x 3
Extruded_32 x 6
User_Library-PowerPAK_SO-8_(S) x 2
Extruded_33
BODY_MAA05 x 2
LEADS_MAA05A_3 x 2
LEADS_MAA05A_4 x 2
LEADS_MAA05A_5 x 2
LEADS_MAA05A_6 x 2
LEADS_MAA05A_7 x 2
BODY_MAA06 x 2
LEADS_MAA06_3 x 2
LEADS_MAA06_4 x 2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

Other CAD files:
hardware/case/cap_and_beagle_board_assembly/R114_2PCB.sldasm
hardware/pcb/Case/cap_and_beagle_board_assembly/C323_1PCB.sldasm
hardware/case/cap_and_beagle_board_assembly/C600_2PCB.sldasm
hardware/pcb/Case/cap_and_beagle_board_assembly/C127_1PCB.sldasm
hardware/case/cap_and_beagle_board_assembly/R203PCB.sldasm
hardware/pcb/Case/cap_and_beagle_board_assembly/C113_2PCB.sldasm
hardware/case/cap_and_beagle_board_assembly/C108_2PCB.sldasm
hardware/pcb/Case/cap_and_beagle_board_assembly/U305_2PCB.sldasm
hardware/case/cap_and_beagle_board_assembly/R310_2PCB.sldasm
hardware/pcb/Case/cap_and_beagle_board_assembly/C114_2PCB.sldasm
hardware/case/cap_and_beagle_board_assembly/User_Library-filterassy-1_cap_top_hat_1.sldprt
hardware/pcb/Case/cap_and_beagle_board_assembly/R202PCB.sldasm
hardware/case/cap_and_beagle_board_assembly/LED201PCB.sldasm
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

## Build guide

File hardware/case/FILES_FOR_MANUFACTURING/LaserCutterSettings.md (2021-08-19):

# Acrylic Cover Laser Cutter/Engraver Settings

Reference: Trotec Speedy 300

1) Black Color
   - Engrave
   - Power = 100
   - Speed = 65
   - 1000 PPI
   - Air = On

2) Red Color
   - Cut
   - Power = 100
   - Speed = 0.35
   - 5000 Hz
   - Air = On

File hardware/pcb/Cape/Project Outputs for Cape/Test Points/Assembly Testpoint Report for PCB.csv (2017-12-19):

Net | Name | X Coord | Y Coord | Side | Hole Size | Type
+6.8V | TP402-1 | 79.3mm | 88.9mm | Bottom | 0mm | Surface mount
-6.8V | TP403-1 | 98.9mm | 84.2mm | Bottom | 0mm | Surface mount
VCOMP+ | TP404-1 | 123.7mm | 99.6mm | Bottom | 0mm | Surface mount
VCOMP- | TP405-1 | 121.3mm | 99.3mm | Bottom | 0mm | Surface mount
-5V | TP406-1 | 139.5mm | 101.5mm | Bottom | 0mm | Surface mount
5V | TP407-1 | 91.8mm | 90.7mm | Bottom | 0mm | Surface mount
VCCA+ | TP408-1 | 127mm | 88.3mm | Bottom | 0mm | Surface mount
VCCA- | TP409-1 | 123.7mm | 105.8mm | Bottom | 0mm | Surface mount
-2.5V | TP410-1 | 120.7mm | 111.2mm | Bottom | 0mm | Surface mount
+2.5V | TP411-1 | 114.4mm | 97.6mm | Bottom | 0mm | Surface mount
V_RAW | TP412-1 | 92.7mm | 77mm | Bottom | 0mm | Surface mount
GND | TP413-1 | 81.1mm | 77.3mm | Bottom | 0mm | Surface mount
ENABLEPOWER | TP414-1 | 83mm | 83.9mm | Bottom | 0mm | Surface mount
3.3V | TP415-1 | 96.7mm | 120.6mm | Bottom | 0mm | Surface mount

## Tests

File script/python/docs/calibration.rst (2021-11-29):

RocketLogger Calibration
========================

The :mod:`rocketlogger.calibration` module provides the support for RocketLogger
device calibration. This calibration data processing support is built around the class
:class:`rocketlogger.calibration.RocketLoggerCalibration`.

To generate a calibration file from your calibration measurements use the RocketLogger:

.. code-block:: python

    >>> from rocketlogger.data import RocketLoggerData
    >>> from rocketlogger.calibration import RocketLoggerCalibration, CALIBRATION_SETUP_SMU2450
    >>> filename_prefix = "20200101_"
    >>> data_i1l = RocketLoggerData(f"{filename_prefix}calibration_i1l.rld")
    >>> data_i2l = RocketLoggerData(f"{filename_prefix}calibration_i2l.rld")
    >>> data_ih = RocketLoggerData(f"{filename_prefix}calibration_ih.rld")
    >>> data_v = RocketLoggerData(f"{filename_prefix}calibration_v.rld")
    >>>
    >>> cal = RocketLoggerCalibration()
    >>> cal.load_measurement_data(
    ...     data_v,
    ...     data_i1l,
    ...     data_ih,
    ...     data_i2l,
    ...     data_ih,
    ... )

or using the shortcut with passing the trace filenames:

.. code-block:: python

    >>> filename_prefix = "20200101_"
    >>> cal = RocketLoggerCalibration(
    ...     f"{filename_prefix}calibration_v.rld",
    ...     f"{filename_prefix}calibration_i1l.rld",
    ...     f"{filename_prefix}calibration_ih.rld",
    ...     f"{filename_prefix}calibration_i2l.rld",
    ...     f"{filename_prefix}calibration_ih.rld",
    ... )

to calculate new calibration parameters and store the files use:

.. code-block:: python

    >>> cal.recalibrate(CALIBRATION_SETUP_SMU2450)
    >>> cal.write_calibration_file("calibration.dat")

it is recommended to print the errors within the calibration data to verify
that the provided calibration measurements were properly recorded:

.. code-block:: python

    >>> cal.print_statistics()

the statistics output can also be save as log file (it is recommend to always
keep a log file along with the calibration):

.. code-block:: python

    >>> cal.write_log_file("calibration.log")

An example script that can be used for performing the calibration
calculations is available in ``create_calibration.py`` distributed with the
source package or available in the package's repository.

Further, the ``convert_calibration.py`` script is available to convert legacy
calibration files used for RocketLogger versions `1.x` to the latest format.

For more details on the individual functions and its optional parameters,
please we refer to the API documentation of the
:class:`rocketlogger.calibration.RocketLoggerCalibration` class.

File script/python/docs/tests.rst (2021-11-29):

Package Tests
=============

The :doc:`tests` module provides the package tests for the
:mod:`rocketlogger.data` and :mod:`rocketlogger.calibration` modules.

The tests are to be executed using the ``nosetests`` and ``coverage`` utilities,
e.g. using the ``test_coverage.sh`` bash script distributed with the package.
Further, the package includes a configuration for ``tox`` to test against all supported Python installations,
and a helper script ``test_performance.py`` to test the performance of various file import options on your target machine

Data Tests
----------

.. automodule:: tests.test_data
    :members:
    :undoc-members:
    :show-inheritance:

Calibration Tests
-----------------

.. automodule:: tests.test_calibration
    :members:
    :undoc-members:
    :show-inheritance:

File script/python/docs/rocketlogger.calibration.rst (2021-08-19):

Calibration Module
==================

The :mod:`rocketlogger.calibration` provides the support for processing calibration measurements,
to calculate calibration parameters, and for generating RocketLogger calibration files.

.. automodule:: rocketlogger.calibration
    :members:
    :undoc-members:
    :show-inheritance:

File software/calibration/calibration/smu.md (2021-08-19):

# SMU2450 Remote Control

**Source:**
SMU2450 Reference Manual p. 3-65ff 
- [Product Page](https://www.tek.com/keithley-source-measure-units/keithley-smu-2400-graphical-series-sourcemeter)
- [Manual Download](https://download.tek.com/manual/2450-901-01_D_May_2015_Ref.pdf)

## Setting up a sweep using TSP commands

To set up a sweep using TSP commands, you send one of the following commands:
- smu.source.sweeplinear(): Sets up a linear sweep for a fixed number of measurement points.
- smu.source.sweeplinearstep(): Sets up a linear source sweep configuration list and trigger model with a fixed number of steps.
- smu.source.sweeplist(): Sets up a sweep based on a configuration list, which allows you to customize the sweep.
- smu.source.sweeplog(): Sets up a logarithmic sweep for a set number of measurement points.

### To create a sweep:
1. Set the source function using smu.source.func.
2. Set the source range using smu.source.range.
3. Set any other source settings that apply to your sweep. You must set source settings before the sweep function is called.
4. If you are using smu.source.sweeplist(), set up the source configuration list for your sweep.
5. Set the parameters for the sweep command.
6. Set the measurement function using smu.measure.func.
7. Set the measurement range using smu.measure.range.
8. Make any other settings appropriate to your sweep.
9. Send trigger.model.initiate() to start the sweep.

### Aborting a sweep
Sweeps can be stopped for the following reasons:
- The limit set by the abort on limit setting was exceeded
- The trigger model is aborted
You can stop the sweep while it is in progress. When you stop the sweep, all sweep commands in the trigger model are terminated.

## Examples

### Linear sweep with a voltage source
The following examples perform a linear sweep that uses a voltage source. They perform the following actions:
- Reset the instrument to its defaults.
- In TSP only, name the configuration list that is created for this sweep RES.
- Set the source function to voltage.
- Set the source range to 20 V.
- Set the source limit for measurements to 0.02 A
- Set the measure function to current.
- Set the current range to automatic.
- Set up a linear sweep that sweeps from 0 to 10 V in 21 steps with a source delay of 200 ms.
- Start the sweeps.
- Wait until all commands are complete and then query the source value and measurement reading.

No buffer is defined, so the data is stored in `defbuffer1`. See Reading buffers (on page 3-10) for more information about reading buffers.

#### Using TSP commands:
```
reset()
smu.measure.func = smu.FUNC_DC_CURRENT
smu.measure.autorange = smu.ON
smu.source.func = smu.FUNC_DC_VOLTAGE
smu.source.range = 20
smu.source.ilimit.level = 0.02
smu.source.sweeplinear("RES", 0, 10, 21, 200e-3)
trigger.model.initiate()
waitcomplete()
printbuffer(1, 21, defbuffer1.sourcevalues, defbuffer1.readings)
```

### Logarithmic sweep with a current source
The following examples perform a logarithmic sweep using a current source. They perform the following actions:
- Reset the instrument to its defaults.
- Set the measure function to current.
- Set the source function to current.
- Set the source range to 100 mA.
- Set up a logarithmic sweep from 100 μA to 100 mA in 10 steps with a source delay of 10 ms, a sweep count of 1, and a fixed source range. In TSP only, name the configuration list that is created for this sweep RES.
- Set the current range to 100 μA.
- Start the sweep.

No buffer is defined, so the data is stored in defbuffer1. See Reading buffers (on page 3-10) for more information on reading buffers.

#### Using TSP commands:
```
reset()
smu.source.func = smu.FUNC_DC_CURRENT
smu.source.range = 100e-3
smu.source.vlimit.level = 20
smu.source.sweeplog("RES", 100e-6, 100e-3, 10, 10e-3)
smu.measure.func = smu.FUNC_DC_VOLTAGE
smu.measure.range = 20
trigger.model.initiate()
waitcomplete()
printbuffer(1, 10, defbuffer1.sourcevalues, defbuffer1.readings)
```

## Function Reference smu.source.sweeplinear():

```
smu.source.sweeplinear(configListName, start, stop, points, delay, count, rangeType, failAbort, dual, bufferName)
```

- _configListName_
  
  A string that contains the name of the configuration list that the instrument will create for this sweep

- _start_
  
  The voltage or current source level at which the sweep starts:
  - Current: -1.05 A to 1.05 A
  - Voltage: -210 V to 210 V

- _stop_
  
  The voltage or current at which the sweep stops:
  - Current: -1.05 A to 1.05 A
  - Voltage: -210 V to 210 V

- _points_
  
  The number of source-measure points between the start and stop values of the sweep (2 to 1e6); to calculate the number of source-measure points in a sweep, use the following formula: `Points = [(Stop - Start) / Step] + 1`

- _delay_
  
  The delay between measurement points; default is `smu.DELAY_AUTO`, which enables autodelay, or a specific delay value from 50 μs to 10 ks, or 0 for no delay.

- _count_
  
  The number of times to run the sweep; default is 1:
  - Infinite loop: `smu.INFINITE`
  - Finite loop: 1 to 268,435,455

- _rangeType_
  The source range that is used for the sweep:
  - Most sensitive source range for each source level in the sweep: `smu.RANGE_AUTO`
  - Best fixed range: `smu.RANGE_BEST` (default)
  - Present source range for the entire sweep: `smu.RANGE_FIXED`

- _failAbort_
  - Complete the sweep if the source limit is exceeded: `smu.OFF`
  - Abort the sweep if the source limit is exceeded: `smu.ON` (default)

- _dual_
  Determines if the sweep runs from start to stop and then from stop to start:
  - Sweep from start to stop only: `smu.OFF` (default)
  - Sweep from start to stop, then stop to start: `smu.ON`

- _bufferName_
  
  The name of a reading buffer; the default buffers (`defbuffer1` or `defbuffer2`) or the name of a user-defined buffer; if no buffer is specified, this parameter defaults to `defbuffer1`

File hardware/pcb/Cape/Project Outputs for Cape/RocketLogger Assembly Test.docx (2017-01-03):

# RocketLogger Assembly Test

## Required Hardware

- One or two power supplies with current limiting and measuring capability

## Multimeter or similar to measure voltages at specified test points

## Instructions

Note: This testing may be done before the headers (P8, P9, and J1) and the SMA connectors are assembled.

1. Connect GND (P9 pins 1, 2 / TP413), all voltages are referenced to this connection
2. Connect 3.3 V (P9 pins 3, 4 / TP415)
  1. Current limit: 20 mA
  2. The idle current draw should be less than 10 mA (measured: 0.27 mA)
  3. The 3.3 V rail may be disconnected
3. Connect 5 V (P9 pins 7, 8 / TP412) using a lab PSU
  1. Current Limit: 1000 mA
  2. The current draw should be close to 0 mA
  3. Keep this rail connected for the remainder of the tests
4. Connect 5 V or 3.3 V to PowerEnable (P9 pin 13 / TP414)
  1. The current draw should be 5mA or 3.3mA respectively (1kΩ resistor to GND)
  2. The current draw on the 5V rail should now be: 135 mA ± 20 mA
  3. Keep the PowerEnable connection for the remainder of the tests
5. Check all the voltage supply test points
  1. TP402: +6.8 V ± 0.3 V
  2. TP403: -6.8 V ± 0.3 V
  3. TP408: +6 V ± 0.25 V
  4. TP409: -6 V ± 0.25 V
  5. TP411: +2.5 V ± 0.1 V
  6. TP410: -2.5 V ± 0.1 V
  7. TP407: +5 V ± 0.15 V
  8. TP406: -5 V ± 0.15 V
6. Check the compensation test points
  1. TP404: +400 mV ± 50 mV
  2. TP405: -400 mV ± 50 mV
7. Disable and disconnect the power supplies

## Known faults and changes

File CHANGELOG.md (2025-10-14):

# Changelog

## Version 2.1.3 (2025-10-14)

* [ADD] Support and test coverage for Python 3.12-3.14
* [ADD] Document and test compatibility of Python support library with numpy 1.26-2.3
* [CHANGED] Update web server dependencies with security patches
* [CHANGED] Update Debian *buster* repositories to the Debian archives 

_Notes:_

This updates web server dependencies with security patches and adapts to archived Debian repositories.
Further, the Python support library adds compatibility and test coverage for latest Python versions and numpy releases.

## Version 2.1.2 (2023-08-01)

* [ADD] Document and test compatibility of Python support library with numpy 1.24 and 1.25
* [ADD] GitLab CI for testing documentation generation (relates to #105)
* [CHANGED] Update web server dependencies with security patches 
* [FIX] Improved SD card mount reliability (#107)
* [FIX] Automated release documentation generation (#105)
* [FIX] Image patching script failure with latest docker images

_Notes:_

This bugfix release address SD card reliability problems, fixes release documentation generation, and updates web server dependencies with security patches.
Further, the compatibility of Python support library with latest numpy releases is tested and documented.

## Version 2.1.1 (2023-07-15)

* [CHANGED] Update to latest Debian *buster* release 10.13 image for security fixes
* [CHANGED] Update web server dependencies for security fixes

_Notes:_

This bugfix release focuses on security updates for web server dependencies and the operating system base image.

## Version 2.1.0 (2023-02-19)

Base operating system:
* [CHANGED] update to Debian *buster* release 10.13 (#78)
* [CHANGED] update to Node.js version 18 LTS (#91)

RocketLogger software:
* [ADDED] System tests for software and data processing pipeline (#73)
* [ADDED] Server side caching of measurement data (#74)
* [ADDED] Activity aware binary channel down-sampling (#92)
* [ADDED] Document measurement status and data stream interface, provide `--stream` CLI alias
* [CHANGED] Improved PWM hardware configuration reliability (#68, #76)
* [CHANGED] Hardware module based inter sample time capturing (#67)
* [CHANGED] Update web interface dependencies to latest version (#71, #83)
* [CHANGED] Optimize and reduce web interface dependencies (#84)
* [CHANGED] Refactor web interface implementation and addition of unit tests (#70, #72)
* [CHANGED] Update development tool configurations (#93, #95)

Python support library:
* [ADDED] Support and test coverage for Python 3.10 and 3.11 (#82, #88)
* [CHANGED] Migrate from nose to pytest (#81)
* [FIX] More robust measurement set-point detection (#94)

_Notes:_

This release updates the base operating and web interface dependencies. New features include server side measurement data caching and "activity aware" down-sampling of digital signal for the web interface preview.
Other notable changes include more robust hardware configuration and initial automated test coverage of the measurement software and web interface components.
Finally, the measurement status and data streaming interfaces are now officially documented for use by third party software.

## Version 2.0.2 (2021-12-09)

RocketLogger software:
* [FIXED] Corrupt RLD files when logging no binary channels (#57)
* [FIXED] Corrupt channel info in split RLD files (#62)

Python support library:
* [ADDED] Standalone script to recover RLD files corrupted by #57
* [FIXED] Missing documentation of file revision changes (#61)
* [CHANGED] Cross validate file headers and tolerate channel info corruption of split files (relates to #62)

_Notes:_

This bugfix release resolves RLD file corruption related issues. Details on how to fully recover affected measurement files are given below.
A timely update is highly recommended to avoid generating corrupt data files.

_Recover Corrupt Data Files:_

Measurement files affected by bugs #57 or #62 can be recovered without data loss:
* To recover files affected by #57 use the `bug57_recover.py` script provided in the Python source package (or available directly from the repository).
* The updated Python library can tolerate channel info header corruption of split files due to bug #62 if all files of the same measurement are imported in one batch.

## Version 2.0.1 (2021-11-29)

RocketLogger software:
* [FIXED] RocketLogger reporting "uncalibrated" after restart (#34)
* [FIXED] Sample aggregation not working, resulting in segmentation fault (#35) by [@rdaforno](https://github.com/rdaforno)
* [FIXED] Sample aggregation "average" produces invalid results (#42) by [@rdaforno](https://github.com/rdaforno)
* [FIXED] Web interface: filename not adjusted when changing file format (#49)
* [FIXED] RocketLogger daemon not terminating on failure (#50)

Python support library:
* [FIXED] Python support calibration conversion script availability documentation (#33)
* [FIXED] Exclude tests from Python package installation (#40)
* [FIXED] Remove debug console output in Python support library (#46)
* [FIXED] Specify exact versions of Python support package dependencies (#48)

_Notes:_

This bugfix release resolves issues related to the sample aggregation for low data rates, the Python support package and the web interface. See the respective bug reports linked in the list above for more details.
Measurements with samples rates <1 kSps, and average aggregation mode (with CLI option `--aggregate=average`)performed with RocketLogger version 2.0.0 and earlier may be corrupted. Users relying on the web interface only and not setting this specific mode as default using the CLI are _not_ affected.

## Version 2.0.0 (2021-08-19)

The changes since version [1.1.6](#version-116-2019-07-31) include all changes of the the beta release [2.0.0-beta1](#version-200-beta1-2021-06-12) and the fixes and improvements listed below.

Base operating system:
* [CHANGED] update to Debian *buster* release 10.10
* [CHANGED] improve robustness and usability of system setup scripts
* [CHANGED] optimize the size of locally patched operating system image
* [FIXED] remote system installation script not working (#25)

RocketLogger software:
* [CHANGED] additional actions available via hardware button gestures
* [FIXED] startup artifacts after RocketLogger system startup or hardware reset (#19)
* [FIXED] segmentation fault in logging output (#29)
* [FIXED] no data plotted in web interface when measuring low current channel only (#26)
* [FIXED] incorrect plot selection shown when reloading web interface (#27)
* [FIXED] invalid configuration in web interface for low sample rates (#31)

Python support library:
* [FIXED] use effectively configured instead of theoretical ADC sample rate for the calculation of relative timestamps _(backward incompatible)_ (#13)
* [FIXED] invalid absolute timestamp calculation for last data block (#30)

Additionally, the documentation in the repository and the accompanying [wiki pages](https://github.com/ETHZ-TEC/RocketLogger/wiki) was updated and significantly extended. These changes address several documentation related issues (#20, #21, #22, #23, #32).

_Notes:_

This major release updates the base operating system to run the latest Debian version and includes numerous internal software and development tool changes. The most noticeable change for the user is the new web control interface that was implemented from scratch and a simplified, more robust command line interface.
The Python support library received new device calibration features and extended data processing functionality.

Due to the major upgrade of the base operating system from Debian version 7 to 10, and the change of the install location to the internal eMMC memory, the RocketLogger system needs to be reinstalled.

_Backward Incompatible Changes:_

* The updated calibration file format requires conversion of existing calibration data when upgrading from previous versions. Follow the [upgrade instructions](https://github.com/ETHZ-TEC/RocketLogger/wiki/upgrade-v2) when updating from RocketLogger version 1.x.
* The new RocketLogger command line interface uses different modes and arguments. The changes are summarized under [CLI update summary](https://github.com/ETHZ-TEC/RocketLogger/wiki/measurement-control#command-line-interface-changes-from-version-1x-to-200).
* The Python Support Library's `get_time()` API has changed. Remove the `absolute_time` argument and use only the updated `time_reference` argument for timestamp reference selection. For detailed API documentation refer to the [Python documentation](https://github.com/ETHZ-TEC/RocketLogger/wiki/python).
* The Python Support Library's `get_time()` implementation for relative timestamp calculation (i.e. using `time_reference="relative"`) has been fixed to use the exact used ADC sample rate instead of the theoretically targeted sample rate. Expect different timestamp values and derived analysis compared to versions 1.x when using `get_time()` with `time_reference="relative"` (corresponding to the default argument value)!
* The MATLAB calibration support has been removed in favor of the new calibration tools included in the Python Support Library.

## Version 2.0.0-beta1 (2021-06-12)

Base operating system:
* [ADDED] local operating system image patching to generate ready to use RocketLogger image (#4)
* [ADDED] switch to Debian *buster* release (#2)
* [CHANGED] install operating system to BeagleBone's embedded eMMC memory, use external SD card for configuration and data storage
* [CHANGED] simplify remote system setup procedure

RocketLogger software:
* [ADDED] use meson build framework for combined build and installation of all software components
* [ADDED] PRU measured ADC sample interval, available as optional `DT` channel (#17)
* [ADDED] switch to ZeroMQ messaging library for data streaming to the webserver
* [ADDED] Node.js based web interface with server side data streaming capability (#3, #5, #9)
* [CHANGED] command line interface update: improved argument consistency and more robust argument parsing _(backward incompatible)_
* [CHANGED] rework low level hardware interfacing for Debian *buster* compatibility (#2)
* [CHANGED] update and reorganize internal software API and headers for increased consistency
* [CHANGED] update to latest and official compiler tools (#18)
* [CHANGED] Binary file format: increment file version to `0x04`
* [REMOVED] legacy web control interface

Python support library:
* [ADDED] extended get data API to access relevant header fields and filenames, add pandas DataFrame generation
* [ADDED] add header-only import, recovery mode for truncated file import
* [ADDED] add calibration support (#10)
* [ADDED] sample data processing and calibration scripts (#7)
* [CHANGED] make plotting an optional feature to reduce package dependencies
* [CHANGED] `get_time()` API: use `time_reference` for timestamp reference selection (using updated parameters!), drop `absolute_time` argument _(backward incompatible)_
* [FIXED] deprecated NumPy API dependency (#12)

MATLAB support:
* [DEPRECATED] The MATLAB support for processing RocketLogger data is deprecated and will be removed in a future release. It is recommended to switch to the more feature-rich Python support library (#11)
* [REMOVED] The MATLAB calibration support has been dropped. Use the Python support library to generate new or convert existing calibration data

_Notes:_

This beta release for the next major version updates the base operating system to run the latest Debian version and includes numerous internal software and development tool changes. The most noticeable change for the user is the new web control interface that was implemented from scratch.
Calibration features were added to the Python support library and the data processing functionality was extended.

Due to the major upgrade of the base operating system from Debian version 7 to 10, and the change of the install location to the internal eMMC memory, the RocketLogger system needs to be reinstalled.

_Known Issues:_

* Unresponsive web interface when system partition is running out of space (#23)
* Startup artifacts after RocketLogger system startup or hardware reset (#19)
* Python library uses target instead of theoretical configured sample rate for relative timestamp calculation (#13)

## Version 1.1.6 (2019-07-31)

* [FIXED] Software: potential corruption of ambient file name (#127)
* [FIXED] Software: typo in ambient file channel name (#128)
* [FIXED] Software: wrong scale for default file split value (#124)
* [CHANGED] Python support: document successfully tested compatibility with recent Python and NumPy releases

_Notes:_

This hotfix release addresses two issues related to storing ambient sensor data and an invalid default value in the measurement file split configuration. The Python support package was tested to successfully work with recent Python and NumPy updates.

## Version 1.1.5 (2019-03-04)

* [FIXED] Software: corrupt data when writing files >2 GB (#119)
* [FIXED] Software/web interface: data aggregation issue for larger time scales (#117)
* [FIXED] Documentation: more detailed description of common measurement setups and user interfaces (#114, #120)
* [CHANGED] Software: split data files at 1 GB by default (relates to #119)

_Notes:_

This hotfix release resolves a file writing issue when saving the measurements to a single large data file and a data aggregation issue in the web interface preview. Furthermore, the documentation in the wiki on measurement setup and control has been updated and extended.

## Version 1.1.4 (2018-06-26)

* [FIXED] Software: corrupt data when using high sampling rates and values are close to full range (#116)
* [FIXED] Python support: single data block file import issue (#115).

_Notes:_

This hotfix release resolves a data wrap-around issue for sampling rates of 32 kSps and 64 kSps and a Python support bug when importing files with a single data block.

## Version 1.1.3 (2018-04-26)

* [FIXED] Software: corrupt low current valid channel when digital channels are disabled (#108)
* [FIXED] Software: invalid lux calculation for mid/high range of TSL4531 (#111)
* [FIXED] Software/web interface: add more detailed version information (#112)
* [FIXED] Software: invalid data block timestamps in sensor file (#113) by [@masoudinejad](https://github.com/masoudinejad)

_Notes:_

This hotfix release resolves an issue with the low current valid channel when disabling digital channels and two bugs related to logging external sensors.
The software now includes the git revision and build date in its version information output.

## Version 1.1.2 (2018-02-26)

* [FIXED] Software: invalid comment length calculation in binary file header (#107)

_Notes:_

This hotfix release fixes a comment length calculation issue that generated invalid files headers for some specific file comment lengths.

## Version 1.1.1 (2018-01-25)

* [FIXED] Python support: overflow in channel merge functionality (#106) by [@AlexRaimondi](https://github.com/AlexRaimondi)
* [FIXED] Python support: specify tested Python dependencies and automated testing for different environments

_Notes:_

This hotfix release fixes a data overflow problem in the Python support library's channel merge functionality that occurs with v1.1 on some platforms.

## Version 1.1 (2017-12-19)

* [FIXED] Hardware: ground loop in cape supply (#97)
* [FIXED] Software/web interface: filename length check (#96)
* [CHANGED] Binary file format: zero based valid link indexing
* [CHANGED] Binary file format: increment file version to `0x03`
* [ADDED] Ambient sensor logging integrated into the main application
* [ADDED] Python support for RocketLogger data file processing
* [ADDED] Command line option to set file comment field
* [ADDED] Command line option to configure mode of data aggregation when using sampling rates lower than native 1 kSPS
* [ADDED] Binary file format: define additional units for storing ambient sensor data
* [ADDED] Binary file format: distinguish between undefined and unit-less data units

_Notes:_

While previous file versions used (undocumented) one-based channel indexing (e.g. for valid links), this was changed to zero-based indexing for consistency reasons and added to the documentation. To reflect this backward incompatible change and format extensions listed above, the file version was incremented to `0x03`. The Python and Matlab analysis scripts were updated to support these changes, while guaranteeing full backward compatibility with files using the older data format.

## Version 1.0 (2017-03-15)

* [ADDED] First publicly available version

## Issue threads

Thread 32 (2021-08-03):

### ISSUE TITLE
RocketLogger setup: does not boot from SD card by default

### ISSUE THREAD

**Issue by rdaforno** [ETHZ-TEC/RocketLogger#32]
The RocketLogger does not seem to boot from the SD card by default. Therefore, in order to flash the system image, the user button needs to be pressed while powering it up.
-> should be mentioned in the readme

**Comment by lsigrist** [comment]
Let me guess: the user button press was required when flashing a BeagleBone Black (we propose to use a BeagleBone Green). The Black and Green variants are known to have different default boot behavior. Nevertheless, the different behavior should be added to the docs.

**Comment by rdaforno** [comment]
No, it was a normal RocketLogger (bb-8) which has a BBG. Strange.

**Comment by lsigrist** [comment]
Installation troubleshooting to be covered as part of the documentation updates #20.

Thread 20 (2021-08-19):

### ISSUE TITLE
Update documentation for release 2.0.0

### ISSUE THREAD

**Issue by lsigrist** [ETHZ-TEC/RocketLogger#20]
Update RocketLogger wiki
- [x] updated data formats
- [x] updated CLI with comparison to version 1.x
- [x] third-party project dependencies included and build dependency or installed as npm dependencies -> in-repo READMEs
- [x] FlockLab 2 integration overview
- [x] review wiki content, identify more required updates
- [x] remote system installation
- [x] update instructions v1.x -> v2.0.0, incl. data SD card setup
- [x] update calibration instruction with Python library usage
- [x] software and Python code documentation pages
- [x] new hardware button interface
- [x] update wiki home with latest links
- [ ] software architecture overview

**Comment by abiri** [comment]
Reviewed documentation in the Wiki, updated READMEs in 8052997cf98481927a98dda034af98a191832957

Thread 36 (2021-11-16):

### ISSUE TITLE
ADC not responsive error

### ISSUE THREAD

**Issue by rdaforno** [ETHZ-TEC/RocketLogger#36]
After a system update (`apt-get dist-upgrade`), the RocketLogger daemon does not start properly. Error message: `ADC not responsive`. 
By adding an additional delay of ~10 seconds [here](https://github.com/ETHZ-TEC/RocketLogger/blob/flocklab/software/rocketlogger/config/rocketlogger.service#L8) at the end, the problem seems to disappear.

This happens with the `flocklab` branch. Not sure whether this problem is specific to Debian 9.

[Fix added to branch `flocklab`](https://github.com/ETHZ-TEC/RocketLogger/commit/21e5db5785055214750d35c0c9196563f2d93483).

**Comment by lsigrist** [comment]
Closing the issue as not reproduced with any official release. The here described problem hinted at a different issues #50 in case of service start up problems, blocking automatic restart in case of start up problems.

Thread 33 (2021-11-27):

### ISSUE TITLE
Pypi rocketlogger-2.0.0-py3-none-any.whl missing convert_calibration.py

### ISSUE THREAD

**Issue by gemarcano** [ETHZ-TEC/RocketLogger#33]
While upgrading my rocketlogger to v2, I did a pip install and noticed that the `convert_calibration.py` script was not installed. I downloaded the wheel from Pypi directly and inspected it , and it only included the dist info plus:
```
__init__.py
calibration.py
data.py
tests/__init__.py
tests/calibration.py
data.py
```

It looks like none of the files listed in the Manifest.in made it into the wheel (not sure how/if Manifest.in is interpreted).

**Comment by lsigrist** [comment]
The files listed in the `Manifest.in` are only considered for the source package source [1]. The sample scripts `calibrate.py`, `convert_calibration.py`, `example.py` and test data contained in the source distribution are however not considered for installation or built distributions such as wheels.
Please extract the required sample or conversion script from the source distribution `rocketlogger-2.0.0.tar.gz` [2]. Alternatively, these files can directly be downloaded from the repository [3].

[1] https://packaging.python.org/guides/distributing-packages-using-setuptools/#manifest-in
[2] https://pypi.org/project/rocketlogger/2.0.0/#files
[3] https://github.com/ETHZ-TEC/RocketLogger/tree/v2.0.0/script/python

**Comment by lsigrist** [comment]
I have reviewed and update the mentioned wiki page, hope is is now more clear how to get the script. As the generated Python docs should also be reviewed prior to a next release, I propose to keep the issue open for this purpose.

Thanks @gemarcano for reporting this shortcoming!

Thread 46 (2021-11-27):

### ISSUE TITLE
Remove debug console output in Python data processing library functionality

### ISSUE THREAD

**Issue by rtrueb** [ETHZ-TEC/RocketLogger#46]
It would be helpful if the [printout](https://github.com/ETHZ-TEC/RocketLogger/blob/master/script/python/rocketlogger/data.py#L1190) of the `merge_channels` function could be disabled (either permanently, via state of the `RocketLoggerData` class, or via a function argument).

**Comment by lsigrist** [comment]
Thanks @rtrueb, this is a very good point. It is probably not the task of a data processing library to print to the console what it is doing. I'd even extend your input to any print statement in `rocketlogger.data` (see list below) and rather make sure that relevant warnings/errors are raised for unexpected behavior/failures. What do you think? Does this match your reasons for raising this issue?

* [\#772](https://github.com/ETHZ-TEC/RocketLogger/blob/master/script/python/rocketlogger/data.py#L772) - drop, this is expected user defined behavior (function arguement)
* [\#924](https://github.com/ETHZ-TEC/RocketLogger/blob/master/script/python/rocketlogger/data.py#L924) - drop, more of a debug output for expected result
* [\#1190](https://github.com/ETHZ-TEC/RocketLogger/blob/master/script/python/rocketlogger/data.py#L1190) - drop, more of a debug output for expected result

**Comment by rtrueb** [comment]
The proposed changes address my issue and make sense from my point of view.

**Comment by lsigrist** [comment]
fix verified using a942b32

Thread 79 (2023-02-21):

### ISSUE TITLE
Feature request: remote access to RocketLogger data through some streaming, machine-readable manner

### ISSUE THREAD

**Issue by gemarcano** [ETHZ-TEC/RocketLogger#79]
Currently, as far as I can tell, RocketLogger data can be accessed through:
 1. Web interface (exposed by the nodejs webserver)
 2. Interactive mode (exposed through ncurses)
 3. Output file (saved to the filesystem)

I don't know of a way to read live data from the RocketLogger and ingest it on a remote computer. For my particular use case, we want to act on data we're sensing from the RocketLogger, and the control software is on the computer that's connected to the RocketLogger. Does functionality like this already exist and I just missed it?

**Comment by jmadden173** [comment]
I would be interested in this as well

**Comment by lsigrist** [comment]
@gemarcano thanks for your question regarding use case that we have not considered so far. Currently, only the three options you listed are provided as public (and documented) interfaces to the measurement data.

However, as of release 2.0 there is an internal (undocumented) interface for streaming measurement data blocks from the RocketLogger measurement binary to the nodejs server. This [ZeroMQ](https://zeromq.org) based interface follows the publisher-subscriber pattern, where the RocketLogger binary publishes a multi-part message for every measurement data block (at the rate configurable via the `--update` argument).

In a nutshell, the ZeroMQ data message structure looks a follows:
1. JSON formatted metadata: measurement data rate, and the sampled channel info (name, scale, unit, bit offset for binary channels)
2. data block timestamps: the same that are stored in the [data file](https://github.com/ETHZ-TEC/RocketLogger/wiki/data-format#channel-data)
3. channel data as signed 32-bit integers: there is an individual message part for each channel, the order is as specified in the metadata
99. last message part: binary channel data aggregated into 32-bit values, same as in the data file format

The use of the interface is probably best illustrated by the following Python script:
```python
import json
import numpy as np
import zmq

# ZeroMQ socket identifier for status publishing
STATUS_SOCKET = "tcp://127.0.0.1:8276"

# ZeroMQ socket identifier for data publishing
DATA_SOCKET = "tcp://127.0.0.1:8277"

# timestamp block data format
DT_TIMESTAMP = np.dtype(
    [
        ("realtime_sec", "<M8[s]"),
        ("realtime_ns", "<m8[ns]"),
        ("monotonic_sec", "<M8[s]"),
        ("monotonic_ns", "<m8[ns]"),
    ]
)


context = zmq.Context()

print("subscribe to RocketLogger data socket")
socket = context.socket(zmq.SUB)
socket.connect(DATA_SOCKET)
socket.subscribe("")

while True:
    message = socket.recv_multipart()

    # 1. JSON channel metadata
    meta = json.loads(message[0])
    print(f"data received: {meta}")

    # 2. data block timestamps
    time = np.frombuffer(message[1], dtype=DT_TIMESTAMP)
    print(f"time: {time}")

    has_binary_channel = False
    channel_index = 2
    # 3. non-digital channels in order of channel metadata
    for channel in meta["channels"]:
        if channel["unit"] == "binary":
            has_binary_channel = True
            continue

        data = np.frombuffer(message[channel_index], dtype="<i4")
        print(channel["name"], data)

        channel_index += 1

    # 4. binary channel bitmaps (if any listed in metadata)
    if has_binary_channel:
        digital = np.frombuffer(message[channel_index], dtype="<u4")
        print(digital)
```

I tested this to work with release 2.0.2 when executing on the RocketLogger system. Remote access of the interface is not supported, as only local connections are accepted. But if you're not afraid of recompiling the rocketlogger binary: with the following patch, connection from any remote host can be accepted:

```diff
diff --git a/software/rocketlogger/rl.h b/software/rocketlogger/rl.h
index b88f347..a1b234d 100644
--- a/software/rocketlogger/rl.h
+++ b/software/rocketlogger/rl.h
@@ -118,9 +118,9 @@
 #define RL_SHMEM_PERMISSIONS 0666
 
 /// ZeroMQ socket identifier for status publishing
-#define RL_ZMQ_STATUS_SOCKET "tcp://127.0.0.1:8276"
+#define RL_ZMQ_STATUS_SOCKET "tcp://*:8276"
 /// ZeroMQ socket identifier for data publishing status
-#define RL_ZMQ_DATA_SOCKET "tcp://127.0.0.1:8277"
+#define RL_ZMQ_DATA_SOCKET "tcp://*:8277"
 
 /**
  * RocketLogger data aggregation modes.
```

**Comment by lsigrist** [comment]
What I skipped in the reply above:

The 2nd half of the connection to the nodejs server is the measurement status interface. On this interface, JSON formatted measurement status info is published on every data block update (measurement config, sample count, etc.).

```python
import json
import zmq

# ZeroMQ socket identifier for status publishing
STATUS_SOCKET = "tcp://127.0.0.1:8276"


context = zmq.Context()

print("subscribe to RocketLogger status socket")
socket = context.socket(zmq.SUB)
socket.connect(STATUS_SOCKET)
socket.subscribe("")

while True:
    message = socket.recv()
    status = json.loads(message)
    print(f"status received: {status}")
```

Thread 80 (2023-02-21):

### ISSUE TITLE
Unable to Calibrate Rocketlogger with Generic SMU

### ISSUE THREAD

**Issue by stevegtaylor** [ETHZ-TEC/RocketLogger#80]
Calibrating a Rocketlogger with a generic SMU (other than Keithley 2450) generates an error in the conversion script

```
Traceback (most recent call last):
  File "/home/user/source/RocketLogger/script/python/./create_calibration.py", line 64, in <module>
    cal.recalibrate(CALIBRATION_SETUP_SMU2450)
  File "/home/user/source/RocketLogger/script/python/rocketlogger/calibration.py", line 552, in recalibrate
    measurement = [
  File "/home/user/source/RocketLogger/script/python/rocketlogger/calibration.py", line 553, in <listcomp>
    _extract_setpoint_measurement(
  File "/home/user/source/RocketLogger/script/python/rocketlogger/calibration.py", line 140, in _extract_setpoint_measurement
    measurement_sweep_start = np.min(measurement_sweep_bound)
  File "<__array_function__ internals>", line 180, in amin
  File "/home/user/source/RocketLogger/.venv/lib/python3.10/site-packages/numpy/core/fromnumeric.py", line 2918, in amin
    return _wrapreduction(a, np.minimum, 'min', axis, None, out,
  File "/home/user/source/RocketLogger/.venv/lib/python3.10/site-packages/numpy/core/fromnumeric.py", line 86, in _wrapreduction
    return ufunc.reduce(obj, axis, dtype, out, **passkwargs)
ValueError: zero-size array to reduction operation minimum which has no identity
```

@jmadden173

**Comment by jmadden173** [comment]
I was a part of trying to calibrate this rocketlogger with @CSEsteve and would like to add a little bit more information. We were using v2 of the firmware and attempted to calibrate using a Keithley 2400 SMU. Since it does not have a way of inputting the number of sample points, so we tried setting the step size to get the specified number of points as specified in the calibration wiki (https://github.com/ETHZ-TEC/RocketLogger/wiki/calibration). If I recall correctly we used step of 0.099 V, 0.0198 mA, and 1.98 mA for voltage, low current, high current channels.

------- Original Message -------

**Comment by lsigrist** [comment]
Hi @CSEsteve, @jmadden173, from the information you provided, I can think two potential problems:

**Measurement setup**
To match the predefined SMU2450 setups you should use steps of 100 mV V, 20 uA, and 2 mA (see also the [definition](https://github.com/ETHZ-TEC/RocketLogger/blob/master/script/python/rocketlogger/calibration.py#L348) of that specific measurement setup).
Alternatively, you can specify your own calibration setup and pass that one to [`recalibrate`](https://ethz-tec.github.io/RocketLogger/python/v2.0.2/rocketlogger.calibration.html#rocketlogger.calibration.RocketLoggerCalibration.recalibrate). I think the [`RocketLoggerCalibrationSetup`](https://ethz-tec.github.io/RocketLogger/python/v2.0.2/rocketlogger.calibration.html#rocketlogger.calibration.RocketLoggerCalibrationSetup) abstraction should allow for quite some flexibility.

**Step to first/after last set-point measurement**
The above, however, does not explain your Python backtrace.
With quite some guessing from my side, it seems that there is no large enough step before the first set-point and after the last set-point. Without a significant*) step before the first and after the last set-point measurement, the calibration sweep is not detected by the script. I suggest to check that when you trigger a calibration measurement the SMU "jumps" from a zero to the first extreme set-point on start and goes back to zero after the last set-point.

If this requirement is already satisfied in your measurements or the problem persists after doing so, it would help if you could share your calibration's measurement data for further debugging.

*) this is currently hard coded as twice the step size of the measurement sweep. This value should be reviewed, as I can think of setups with only few set-points where the sweep might not be detected (but this is likely not the problem here).

**Comment by lsigrist** [comment]
The latest release 2.1.0 provides improved calibration set-point detection. Therefore closing this for now. Feel free to (re-)open an issue in case of further questions.

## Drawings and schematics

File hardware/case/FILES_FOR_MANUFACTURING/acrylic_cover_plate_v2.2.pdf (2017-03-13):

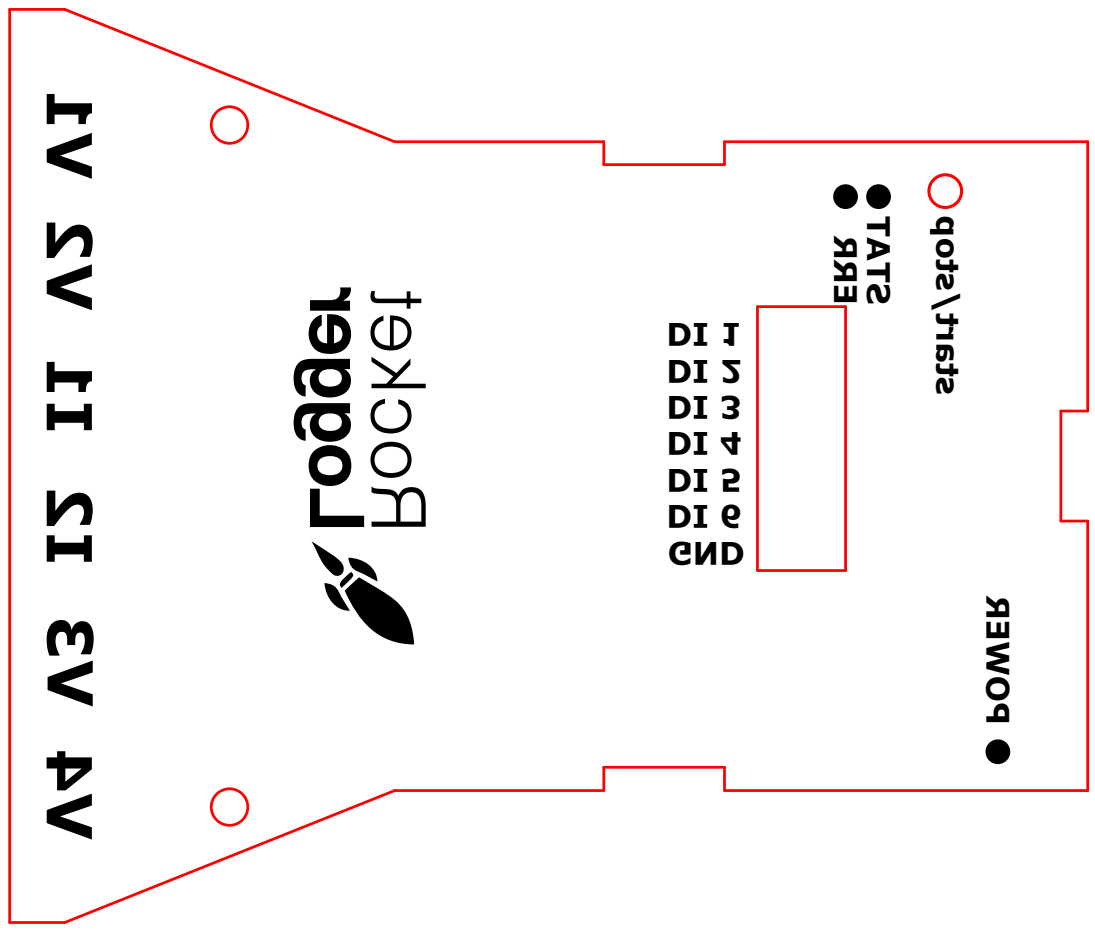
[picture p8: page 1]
start/stop; POWER; GND; ERR; STAT

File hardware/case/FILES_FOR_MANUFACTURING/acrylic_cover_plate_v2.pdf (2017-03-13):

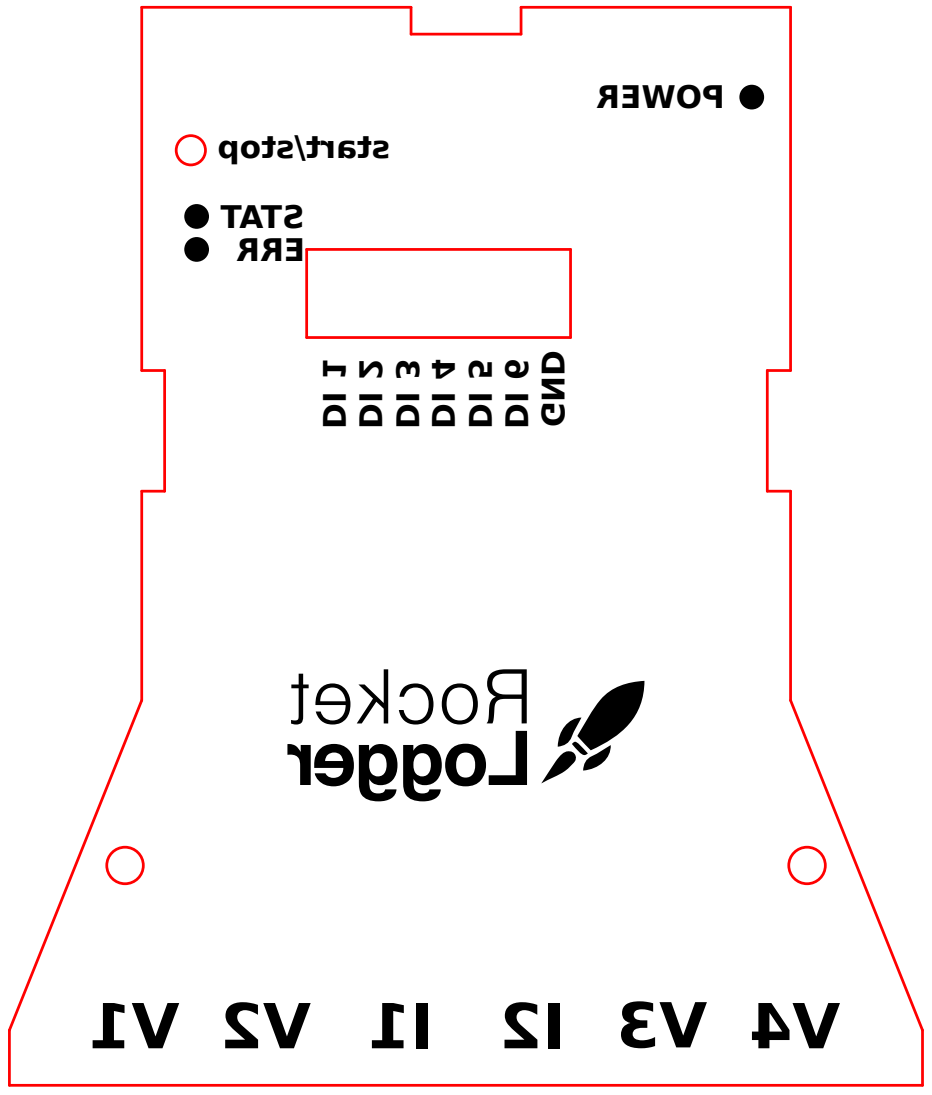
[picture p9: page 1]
GND

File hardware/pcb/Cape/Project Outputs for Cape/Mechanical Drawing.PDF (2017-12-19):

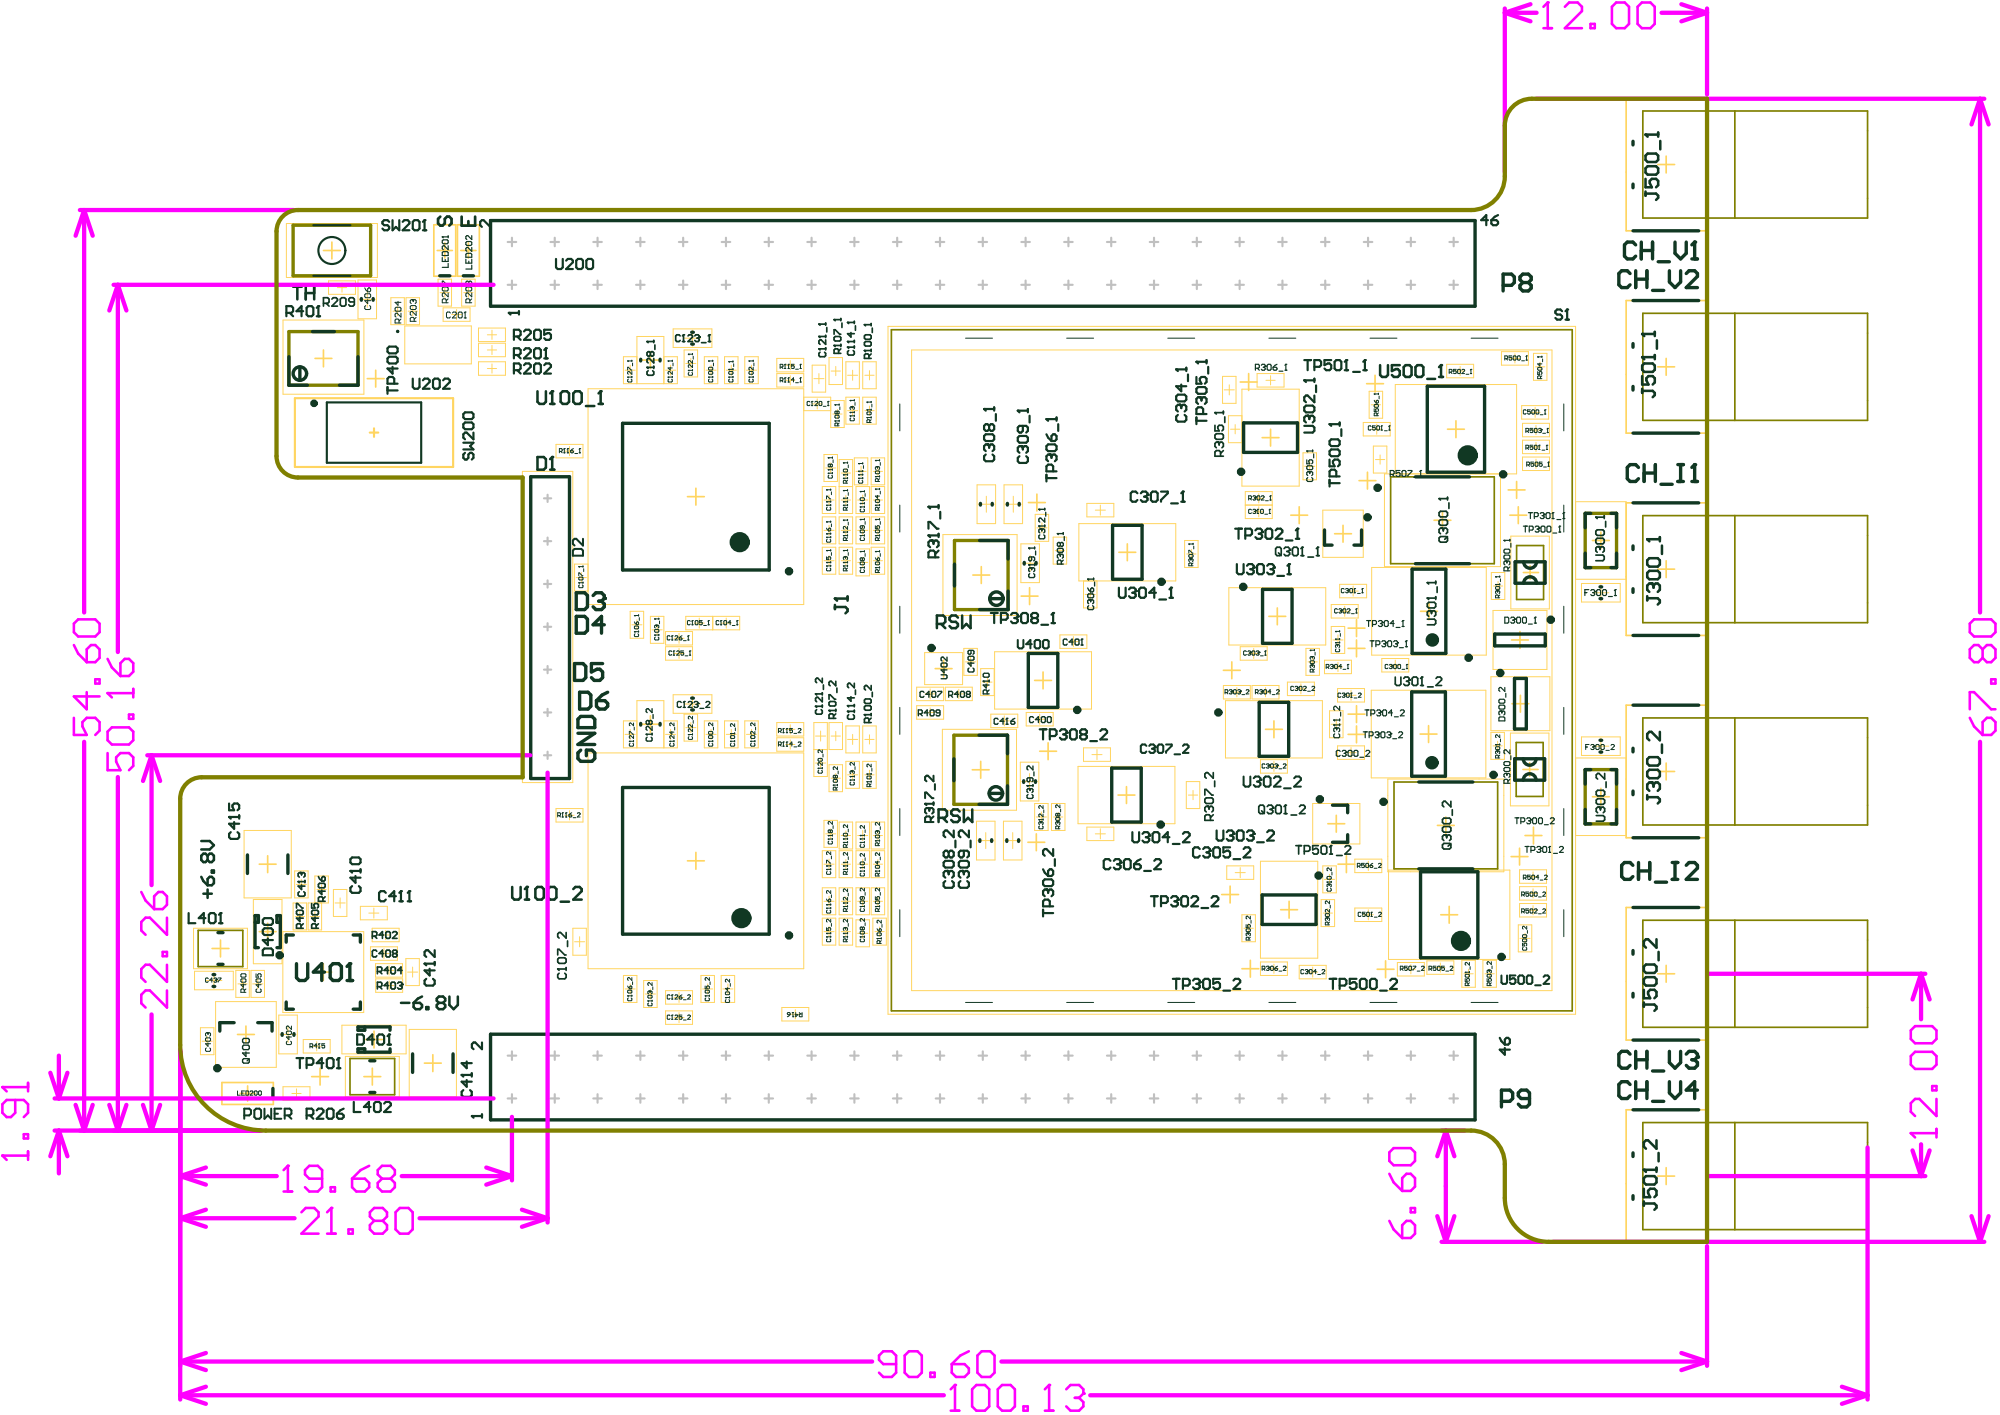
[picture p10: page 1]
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

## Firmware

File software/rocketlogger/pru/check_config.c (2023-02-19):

/**
 * Copyright (c) 2016-2020, ETH Zurich, Computer Engineering Group
 * All rights reserved.
 *
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
 * * Neither the name of the copyright holder nor the names of its
 *   contributors may be used to endorse or promote products derived from
 *   this software without specific prior written permission.
 *
 * THIS SOFTWARE IS PROVIDED BY THE COPYRIGHT HOLDERS AND CONTRIBUTORS "AS IS"
 * AND ANY EXPRESS OR IMPLIED WARRANTIES, INCLUDING, BUT NOT LIMITED TO, THE
 * IMPLIED WARRANTIES OF MERCHANTABILITY AND FITNESS FOR A PARTICULAR PURPOSE
 * ARE DISCLAIMED. IN NO EVENT SHALL THE COPYRIGHT HOLDER OR CONTRIBUTORS BE
 * LIABLE FOR ANY DIRECT, INDIRECT, INCIDENTAL, SPECIAL, EXEMPLARY, OR
 * CONSEQUENTIAL DAMAGES (INCLUDING, BUT NOT LIMITED TO, PROCUREMENT OF
 * SUBSTITUTE GOODS OR SERVICES; LOSS OF USE, DATA, OR PROFITS; OR BUSINESS
 * INTERRUPTION) HOWEVER CAUSED AND ON ANY THEORY OF LIABILITY, WHETHER IN
 * CONTRACT, STRICT LIABILITY, OR TORT (INCLUDING NEGLIGENCE OR OTHERWISE)
 * ARISING IN ANY WAY OUT OF THE USE OF THIS SOFTWARE, EVEN IF ADVISED OF THE
 * POSSIBILITY OF SUCH DAMAGE.
 */

#include <stddef.h>
#include <stdint.h>
#include <stdio.h>
#include <stdlib.h>

#include <fcntl.h>
#include <sys/mman.h>
#include <sys/stat.h>
#include <sys/types.h>
#include <unistd.h>


// Clock Management module register base addresses, offsets and sizes
/// CM_PER register base address
#define CM_PER_BASE 0x44E00000
#define CM_PER_SIZE 0x0400

#define L4LS_CLKSTCTRL_OFFSET       0x00
#define L4LS_CLKCTRL_OFFSET         0x60
#define EPWMSS1_CLKCTRL_OFFSET      0xCC
#define EPWMSS0_CLKCTRL_OFFSET      0xD4
#define EPWMSS2_CLKCTRL_OFFSET      0xD8
#define PRU_ICSS_CLKCTRL_OFFSET     0xE8


// CONTROL module register base addresses, offsets and sizes
/// CONTROL register base address
#define CONTROL_BASE            0x44E10000
#define CONTROL_SIZE            0x20000

#define PWMSS_CTRL_OFFSET       0x664
#define CONF_GMPC_AD14_OFFSET   0x838   /* nDR1 pin, PRU0 controlled */
#define CONF_GMPC_AD15_OFFSET   0x83C   /* nDR0 pin, MUX_MODE6 for PRU0 controlled, MUX_MODE5 for pr1_ecap0_ecap_capin_apwm_o */
#define CONF_GMPC_A2_OFFSET     0x848   /* Latch reset A pin, ehrpwm1A controlled */
#define CONF_GMPC_A3_OFFSET     0x84C   /* Latch reset B pin, ehrpwm1B controlled */
#define CONF_SPI0_SCLK_OFFSET   0x950   /* ADC clock pin, ehrpwm0A controlled */

// PWM module register base addresses, offsets and sizes
/// PWM0 register base address
#define PWM0_BASE 0x48300000
/// PWM1 register base address
#define PWM1_BASE 0x48302000
/// PWM2 module base address
#define PWM2_BASE 0x48304000

/// PWMSS module register offset
#define PWMSS_OFFSET 0x0000
/// eCAP module register offset
#define ECAP_OFFSET 0x0100
/// eQEP module register offset
#define EQEP_OFFSET 0x0180
/// ePWM module register offset
#define EPWM_OFFSET 0x0200

/// PWM module register map size
#define PWM_SIZE 0x0260
/// PWMSS module register map size
#define PWMSS_SIZE 0x0100
/// eCAP module register map size
#define ECAP_SIZE 0x0080
/// eQEP module register map size
#define EQEP_SIZE 0x0080
/// ePWM module register map size
#define EPWM_SIZE 0x0060

// PWMSS sub-module register base addresses, offsets and sizes

/// PWMSS0 register base address
#define PWMSS0_BASE (PWM0_BASE + PWMSS_OFFSET)
/// PWMSS1 register base address
#define PWMSS1_BASE (PWM1_BASE + PWMSS_OFFSET)
/// PWMSS2 module register offset
#define PWMSS2_BASE (PWM2_BASE + PWMSS_OFFSET)

// ePWM sub-module register base addresses, offsets and sizes
/// ePWM0 register base address
#define EPWM0_BASE (PWM0_BASE + EPWM_OFFSET)
/// ePWM1 register base address
#define EPWM1_BASE (PWM1_BASE + EPWM_OFFSET)
/// ePWM2 register base address
#define EPWM2_BASE (PWM2_BASE + EPWM_OFFSET)

// PWMSS configuration register offsets
/// IP Revision Register
#define PWMSS_IDVER_OFFSET 0x00
/// System Configuration Register
#define PWMSS_SYSCONFIG_OFFSET 0x04
/// Clock Configuration Register
#define PWMSS_CLKCONFIG_OFFSET 0x08
/// Clock Status Register
#define PWMSS_CLKSTATUS_OFFSET 0x0C

// ePWM configuration register offsets
/// Time-Base Control Register
#define EPWM_TBCTL_OFFSET 0x00
/// Time-Base Status Register
#define EPWM_TBSTS_OFFSET 0x02
/// Time-Base Phase Register
#define EPWM_TBPHS_OFFSET 0x06
/// Time-Base Counter Register
#define EPWM_TBCNT_OFFSET 0x08
/// Time-Base Period Register
#define EPWM_TBPRD_OFFSET 0x0A
/// Counter-Compare Control Register
#define EPWM_CMPCTL_OFFSET 0x0E
/// Counter-Compare A Register
#define EPWM_CMPA_OFFSET 0x12
/// Counter-Compare B Register
#define EPWM_CMPB_OFFSET 0x14
/// Action-Qualifier Control Register for Output A (EPWMxA)
#define EPWM_AQCTLA_OFFSET 0x16
/// Action-Qualifier Control Register for Output B (EPWMxB)
#define EPWM_AQCTLB_OFFSET 0x18

/// Program main fuction
int main() {
    /// Physical memory file descriptor
    int mem_fd = -1;
    /// Pointer to CM_PER registers
    volatile uint8_t const *cm_per_mem = NULL;
    /// Pointer to CONTROL registers
    volatile uint8_t const *control_mem = NULL;
    /// Pointer to PWM0 registers
    volatile uint8_t const *pwm0_mem = NULL;
    /// Pointer to PWM1 registers
    volatile uint8_t const *pwm1_mem = NULL;

    // open /dev/mem for memory mapping
    mem_fd = open("/dev/mem", O_RDWR | O_SYNC);
    if (mem_fd < 0) {
        return EXIT_FAILURE;
    }

    // map CM_PER registers
    cm_per_mem = (volatile uint8_t const *)mmap(0, CM_PER_SIZE, PROT_READ | PROT_WRITE,
                                        MAP_SHARED, mem_fd, CM_PER_BASE);
    if ((void *)cm_per_mem == MAP_FAILED) {
        return EXIT_FAILURE;
    }

    // map CONTROL registers
    control_mem = (volatile uint8_t const *)mmap(0, CONTROL_SIZE, PROT_READ | PROT_WRITE,
                                        MAP_SHARED, mem_fd, CONTROL_BASE);
    if ((void *)control_mem == MAP_FAILED) {
        return EXIT_FAILURE;
    }

    // map PWM0 registers
    pwm0_mem = (volatile uint8_t const *)mmap(0, PWM_SIZE, PROT_READ | PROT_WRITE,
                                        MAP_SHARED, mem_fd, PWM0_BASE);
    if ((void *)pwm0_mem == MAP_FAILED) {
        return EXIT_FAILURE;
    }

    // map PWM1 registers
    pwm1_mem = (volatile uint8_t const *)mmap(0, PWM_SIZE, PROT_READ | PROT_WRITE,
                                        MAP_SHARED, mem_fd, PWM1_BASE);
    if ((void *)pwm1_mem == MAP_FAILED) {
        return EXIT_FAILURE;
    }

    // read memory mapped registers

    // get pointers of CM_PER registers
    volatile uint32_t const *cm_per_l4ls_clkstctrl =
        (volatile uint32_t const *)(cm_per_mem + L4LS_CLKSTCTRL_OFFSET);
    volatile uint32_t const *cm_per_l4ls_clkctrl =
        (volatile uint32_t const *)(cm_per_mem + L4LS_CLKCTRL_OFFSET);
    volatile uint32_t const *cm_per_epwmss0_clkctrl =
        (volatile uint32_t const *)(cm_per_mem + EPWMSS0_CLKCTRL_OFFSET);
    volatile uint32_t const *cm_per_epwmss1_clkctrl =
        (volatile uint32_t const *)(cm_per_mem + EPWMSS1_CLKCTRL_OFFSET);
    volatile uint32_t const *cm_per_epwmss2_clkctrl =
        (volatile uint32_t const *)(cm_per_mem + EPWMSS2_CLKCTRL_OFFSET);
    volatile uint32_t const *cm_per_pru_icss_clkctrl =
        (volatile uint32_t const *)(cm_per_mem + PRU_ICSS_CLKCTRL_OFFSET);

    printf("CM_PER registers:\n");
    printf("  L4LS_CLKSTCTRL:  \t0x%08x\n", *cm_per_l4ls_clkstctrl);
    printf("  L4LS_CLKCTRL:    \t0x%08x\n", *cm_per_l4ls_clkctrl);
    printf("  EPWMSS0_CLKCTRL: \t0x%08x\n", *cm_per_epwmss0_clkctrl);
    printf("  EPWMSS1_CLKCTRL: \t0x%08x\n", *cm_per_epwmss1_clkctrl);
    printf("  EPWMSS2_CLKCTRL: \t0x%08x\n", *cm_per_epwmss2_clkctrl);
    printf("  PRU_ICSS_CLKCTRL:\t0x%08x\n", *cm_per_pru_icss_clkctrl);

    // get pointers of CONTROL registers
    volatile uint32_t const *control_pwmss_ctrl =
        (volatile uint32_t const *)(control_mem + PWMSS_CTRL_OFFSET);
    volatile uint32_t const *control_conf_gpmc_ad14 =
        (volatile uint32_t const *)(control_mem + CONF_GMPC_AD14_OFFSET);
    volatile uint32_t const *control_conf_gpmc_ad15 =
        (volatile uint32_t const *)(control_mem + CONF_GMPC_AD15_OFFSET);
    volatile uint32_t const *control_conf_gpmc_a2 =
        (volatile uint32_t const *)(control_mem + CONF_GMPC_A2_OFFSET);
    volatile uint32_t const *control_conf_gpmc_a3 =
        (volatile uint32_t const *)(control_mem + CONF_GMPC_A3_OFFSET);
    volatile uint32_t const *control_conf_spi0_sclk =
        (volatile uint32_t const *)(control_mem + CONF_SPI0_SCLK_OFFSET);

    printf("CONTROL registers:\n");
    printf("  PWMSS_CTRL:    \t0x%08x\n", *control_pwmss_ctrl);
    printf("  CONF_GMPC_AD14:\t0x%08x (ADC1 nDR)\n", *control_conf_gpmc_ad14);
    printf("  CONF_GMPC_AD15:\t0x%08x (ADC0 nDR)\n", *control_conf_gpmc_ad15);
    printf("  CONF_GMPC_A2:  \t0x%08x (LATCH A reset)\n", *control_conf_gpmc_a2);
    printf("  CONF_GMPC_A3:  \t0x%08x (LATCH B reset)\n", *control_conf_gpmc_a3);
    printf("  CONF_SPI0_SCLK:\t0x%08x (ADC clock)\n", *control_conf_spi0_sclk);

    // get pointers of PWMSS0 registers
    volatile uint32_t const *pwmss0_sysconfig =
        (volatile uint32_t const *)(pwm0_mem + PWMSS_OFFSET + PWMSS_SYSCONFIG_OFFSET);
    volatile uint32_t const *pwmss0_clkconfig =
        (volatile uint32_t const *)(pwm0_mem + PWMSS_OFFSET + PWMSS_CLKCONFIG_OFFSET);
    volatile uint32_t const *pwmss0_clkstatus =
        (volatile uint32_t const *)(pwm0_mem + PWMSS_OFFSET + PWMSS_CLKSTATUS_OFFSET);

    volatile uint16_t const *epwm0_tbctl =
        (volatile uint16_t const *)(pwm0_mem + EPWM_OFFSET + EPWM_TBCTL_OFFSET);
    volatile uint16_t const *epwm0_tbcnt =
        (volatile uint16_t const *)(pwm0_mem + EPWM_OFFSET + EPWM_TBCNT_OFFSET);
    volatile uint16_t const *epwm0_tbprd =
        (volatile uint16_t const *)(pwm0_mem + EPWM_OFFSET + EPWM_TBPRD_OFFSET);
    volatile uint16_t const *epwm0_cmpa =
        (volatile uint16_t const *)(pwm0_mem + EPWM_OFFSET + EPWM_CMPA_OFFSET);
    volatile uint16_t const *epwm0_cmpb =
        (volatile uint16_t const *)(pwm0_mem + EPWM_OFFSET + EPWM_CMPB_OFFSET);
    volatile uint16_t const *epwm0_aqctla =
        (volatile uint16_t const *)(pwm0_mem + EPWM_OFFSET + EPWM_AQCTLA_OFFSET);
    volatile uint16_t const *epwm0_aqctlb =
        (volatile uint16_t const *)(pwm0_mem + EPWM_OFFSET + EPWM_AQCTLB_OFFSET);

    printf("PWMSS0 registers:\n");
    printf("  SYSCONFIG: \t0x%08x\n", *pwmss0_sysconfig);
    printf("  CLKCONFIG: \t0x%08x\n", *pwmss0_clkconfig);
    printf("  CLKSTATUS: \t0x%08x\n", *pwmss0_clkstatus);
    printf(" ePWM0 registers:\n");
    printf("  TBCTL: \t0x%04x\n", *epwm0_tbctl);
    printf("  TBCNT: \t0x%04x\n", *epwm0_tbcnt);
    printf("  TBPRD: \t0x%04x\n", *epwm0_tbprd);
    printf("  CMPA:  \t0x%04x\n", *epwm0_cmpa);
    printf("  CMPB:  \t0x%04x\n", *epwm0_cmpb);
    printf("  AQCTLA:\t0x%04x\n", *epwm0_aqctla);
    printf("  AQCTLB:\t0x%04x\n", *epwm0_aqctlb);

    // get pointers of PWMSS1 registers
    volatile uint32_t const *pwmss1_sysconfig =
        (volatile uint32_t const *)(pwm1_mem + PWMSS_OFFSET + PWMSS_SYSCONFIG_OFFSET);
    volatile uint32_t const *pwmss1_clkconfig =
        (volatile uint32_t const *)(pwm1_mem + PWMSS_OFFSET + PWMSS_CLKCONFIG_OFFSET);
    volatile uint32_t const *pwmss1_clkstatus =
        (volatile uint32_t const *)(pwm1_mem + PWMSS_OFFSET + PWMSS_CLKSTATUS_OFFSET);
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

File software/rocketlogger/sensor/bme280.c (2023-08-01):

/**
 * Copyright (c) 2016-2020, ETH Zurich, Computer Engineering Group
 * All rights reserved.
 *
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
 * * Neither the name of the copyright holder nor the names of its
 *   contributors may be used to endorse or promote products derived from
 *   this software without specific prior written permission.
 *
 * THIS SOFTWARE IS PROVIDED BY THE COPYRIGHT HOLDERS AND CONTRIBUTORS "AS IS"
 * AND ANY EXPRESS OR IMPLIED WARRANTIES, INCLUDING, BUT NOT LIMITED TO, THE
 * IMPLIED WARRANTIES OF MERCHANTABILITY AND FITNESS FOR A PARTICULAR PURPOSE
 * ARE DISCLAIMED. IN NO EVENT SHALL THE COPYRIGHT HOLDER OR CONTRIBUTORS BE
 * LIABLE FOR ANY DIRECT, INDIRECT, INCIDENTAL, SPECIAL, EXEMPLARY, OR
 * CONSEQUENTIAL DAMAGES (INCLUDING, BUT NOT LIMITED TO, PROCUREMENT OF
 * SUBSTITUTE GOODS OR SERVICES; LOSS OF USE, DATA, OR PROFITS; OR BUSINESS
 * INTERRUPTION) HOWEVER CAUSED AND ON ANY THEORY OF LIABILITY, WHETHER IN
 * CONTRACT, STRICT LIABILITY, OR TORT (INCLUDING NEGLIGENCE OR OTHERWISE)
 * ARISING IN ANY WAY OUT OF THE USE OF THIS SOFTWARE, EVEN IF ADVISED OF THE
 * POSSIBILITY OF SUCH DAMAGE.
 */

#include <errno.h>
#include <stdint.h>
#include <string.h>

#include <i2c/smbus.h>

#include "../log.h"
#include "sensor.h"

#include "bme280.h"

/**
 * List of potentially connected BME280 sensors.
 */
const int bme280_sensors[] = BME280_I2C_ADDRESSES;

/**
 * Get the device ID.
 *
 * @return Returns device ID on success, negative on failure with errno set
 * accordingly
 */
int bme280_get_id(void);

/**
 * Read the sensor specific calibration values.
 *
 * @param sensor_identifier The I2C address of the sensor
 * @return Returns 0 on success, negative on failure with errno set accordingly
 */
int bme280_read_calibration(int sensor_identifier);

/**
 * Set the sensor parameter to default for continuous sensing.
 *
 * @param sensor_identifier The I2C address of the sensor
 * @return Returns 0 on success, negative on failure with errno set accordingly
 */
int bme280_set_parameters(int sensor_identifier);

/**
 * Get the index of the sensor with specified address.
 *
 * @param sensor_identifier The sensor address used to look up the index
 * @return Returns 0 on success, or -1 if sensor with given index was not found
 */
int bme280_get_index(int sensor_identifier);

/**
 * Get fine grained temperature compensation value for further processing.
 *
 * @param sensor_identifier The I2C address of the sensor
 * @param temperature_raw The raw temperature reading
 * @return Fine grained, compensated temperature (arbitrary unit)
 */
static int32_t bme280_compensate_temperature_fine(int sensor_identifier,
                                                  int32_t temperature_raw);

/**
 * Get the compensated temperature in milli degree centigrade.
 *
 * @param sensor_identifier The I2C address of the sensor
 * @param temperature_raw The raw temperature reading
 * @return The compensated temperature in 0.001 degree centigrade
 */
static int32_t bme280_compensate_temperature(int sensor_identifier,
                                             int32_t temperature_raw);

/**
 * Get the compensated pressure in milli Pascal.
 *
 * @param sensor_identifier The I2C address of the sensor
 * @param pressure_raw The raw pressure reading
 * @param temperature_raw The raw temperature reading
 * @return The compensated pressure in 0.001 Pascal
 */
static uint32_t bme280_compensate_pressure(int sensor_identifier,
                                           int32_t pressure_raw,
                                           int32_t temperature_raw);
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

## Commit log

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2016-10-05 Move pcb folder to hardware
    [Bill of Materials-Cape-Octopart.xlsx, Bill of Materials-Cape-Prototype.xlsx, Bill of Materials-Cape-pcbpool.xlsx, Bill of Materials-Cape.xls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]
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2016-10-14 Replace low ppm resistors
    [Bill of Materials-Cape-Prototype.xlsx, current_channel.SchDoc, voltage_channel.SchDoc]
2016-10-14 Slight update to PCB, generate new assembly files
    [PCB_Copper_Signal_1.gbr, PCB_Copper_Signal_2.gbr, PCB_Copper_Signal_3.gbr, PCB_Copper_Signal_4.gbr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]
2016-10-14 BOM for pcbcart
    [Bill of Materials-Cape-Octopart_v0_2_1.xlsx, Bill of Materials-Cape-pcbcart_0_2_1.xlsx]
2016-10-14 New production data *with* polygon fills
    [Bill of Materials-Cape.xls, PCB_Copper_Signal_1.gbr, PCB_Copper_Signal_2.gbr, PCB_Copper_Signal_3.gbr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]
2016-10-14 BOM for pcbway
    [Bill of Materials-Cape-pcbway.xlsx]
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2016-10-14 Add drill drawings
    [PCB_Copper_Signal_1.gbr, PCB_Copper_Signal_2.gbr, PCB_Copper_Signal_3.gbr, PCB_Copper_Signal_4.gbr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]
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2016-10-17 Generate RS-274X files as well
    [PCB.GBL, PCB.GBO, PCB.GBP, PCB.GBS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]
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2016-10-18 Add NC drill files
    [PCB_Mechanical_4.gbr]
2016-10-18 Update BOM, incorporate fixes from/for prototype. Generate new PDF Fixes #3, fixes #9
    [Bill of Materials-Cape.xls, Cape.PrjPcb, cape.SchDoc, current_channel.SchDoc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]
2016-10-18 Change labels for digital inputs, fixes #11
    [Cape.PrjPcb]
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2016-10-19 Change pull-down resistors to pull-up resistors on latch resets
    [Cape.PrjPcb, range_valid_stretching.SchDoc]
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2016-10-26 Connect -2.5V LDO input to -5V instead of -6.8V
    [psu.SchDoc]
2016-10-26 Add input protection to digital inputs
    [digital_voltage_channel.SchDoc]
2016-10-26 Add 2x 100uF input capacitance
    [psu.SchDoc]
2016-10-26 Add testpoints for GND, V_RAW and PowerEnable
    [psu.SchDoc]
2016-10-26 Insert PMOS before VIN_POS to allow the PMIC to disable the +6.8V rail
    [Cape.PrjPcb, cape.SchDoc, psu.SchDoc]
2016-10-26 Fix enable PMOS gate capacitance (connect it between gate and source)
    [psu.SchDoc]
2016-10-26 Use vault component for PMOS
    [Cape.PrjPcb, psu.SchDoc]
2016-10-26 Add designators for fuse and filter on schematic
    [current_channel.SchDoc]
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2016-10-27 Fix problem with latch reset pull-ups
    [range_valid_stretching.SchDoc]
2016-10-27 Remove medium current range
    [Cape.PrjPcb, adc.SchDoc, current_channel.SchDoc, top.SchDoc]
2016-10-27 Change Net Class designators name to 'power'
    [cape.SchDoc, psu.SchDoc]
2016-10-27 Fix unconnected issue in psu.SchDoc
    [psu.SchDoc]
2016-10-27 Remove medium range diodes as well
    [adc.SchDoc]
2016-10-27 Use high density footprint for R415
    [psu.SchDoc]
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2016-10-28 Fixed seg fault (file sample)
2016-10-28 Inserted write status -> no shm start error
2016-10-28 fixed web status prints
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2016-11-01 Add 3.3V testpoint
    [psu.SchDoc]
2016-11-01 Add AssemblyTP net class
    [psu.SchDoc]
2016-11-01 Check testpoints on PCB and add rule, add test point report output (which is rather useless)
    [Assembly Testpoint Report for PCB.csv, Cape.PrjPcb]
2016-11-01 Change current low range gain resistor and range switching point resistor dividers
    [current_channel.SchDoc]
2016-11-01 Remove net antennae from removed medium range
    [Cape.PrjPcb]
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2016-11-02 Minor changes to overlay and assembly drawings
    [Cape.PrjPcb]
2016-11-03 Update BOM entry for BB connectors, improve 3D output, add 2nd 3D output
    [Cape.PrjPcb, cape.SchDoc]
2016-11-03 Update digital input header, add new libraries
    [top.SchDoc]
2016-11-03 Add missing pull-down resistor to PowerEnable
    [Cape.PrjPcb, cape.SchDoc, psu.SchDoc]
2016-11-03 Use 3.9k resistors instead of 3.92k resistors
    [voltage_channel.SchDoc]
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2016-11-03 Generate production outputs
    [Assembly Testpoint Report for PCB.csv, Bill of Materials-Cape.xls, PCB.GBL, PCB.GBO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]
2016-11-03 Change passives BOM entries
    [Bill of Materials-Cape.xls, Cape.PrjPcb, adc.SchDoc, current_channel.SchDoc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]
2016-11-03 Fixed web current merging
2016-11-03 Fix incorrect description for 100uF capacitors
    [Bill of Materials-Cape.xls, psu.SchDoc]
2016-11-04 Add octopart export, pcbcart version
    [Bill of Materials-Cape-Octopart_v1.xlsx, Bill of Materials-Cape-pcbcart_v1.xlsx]
2016-11-04 Fix encoding errors
    [Bill of Materials-Cape-pcbcart_v1.xlsx]
2016-11-04 BOM, add header note to Assembly Test instructions
    [Bill of Materials-Cape-pcbcart_v1.xlsx]
2016-11-04 Generate consistent design data
    [Bill of Materials-Cape.xls, PCB.GBL, PCB.GBO, PCB.GTL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]
2016-11-04 Remove old BOMs
    [Bill of Materials-Cape-Octopart.xlsx, Bill of Materials-Cape-Octopart_v0_2_1.xlsx, Bill of Materials-Cape-pcbcart_0_2_1.xlsx, Bill of Materials-Cape-pcbway.xlsx]
2016-11-04 Remove old pcbpool BOM
    [Bill of Materials-Cape-pcbpool.xlsx]
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2016-11-09 Fixed sample_rate value issue
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2016-11-09 Add BOM for probes
    [BOM.xlsx]
2016-11-10 Add mini hooks to BOM
    [BOM.xlsx]
2016-11-11 Updated BOM from octopart (comments from pcbcart)
    [Bill of Materials-Cape-Octopart_v1.xlsx]
2016-11-14 Fixed wrong web samples taken, moved client notify to pru
2016-11-14 Update BOM description for 100uF capacitors
    [psu.SchDoc]
2016-11-14 Make Voltage Channel naming more consistent
    [adc.SchDoc, top.SchDoc, voltage_channel.SchDoc]
2016-11-14 Lock part IDs of swapped components to prevent problems with annotation
    [Cape.PrjPcb, current_channel.SchDoc, digital_voltage_channel.SchDoc, voltage_channel.SchDoc]
2016-11-14 Update PCB, regenerate BOM (new 100uF entry)
    [Bill of Materials-Cape.xls, Cape.PrjPcb]
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2016-11-14 Remove old, unused libraries
    [Cape.PrjPcb]
2016-11-14 More documentation in the schematic, update some numbers
    [adc.SchDoc, cape.SchDoc, current_channel.SchDoc, psu.SchDoc]
2016-11-14 Update revision number, generate new PDF
    [Cape.PrjPcb, adc.SchDoc, cape.SchDoc, current_channel.SchDoc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]
2016-11-14 Remove empty element for medium range from calibration array, fixes #50
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2016-11-16 Change documentation for current channel gains in schematic
    [Cape.PrjPcb, current_channel.SchDoc]
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2016-11-16 Try to implement genetic search for calibration values, doesn't work reliably
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2016-11-23 Fixed 100s/div current merge prob
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2016-12-01 New statusreceived func, fixed key filter
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2016-12-02 add better time handling with externa accessible sampling time fix relative time: first sample has zero time offset
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2016-12-20 3d case by dominic
    [132322.sldasm, 416131160802.sldasm, 761606048.sldasm, 761608904.sldasm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]
2016-12-20 copy to case folder
    [132322.sldasm, 416131160802.sldasm, 761606048.sldasm, 761608904.sldasm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]
2016-12-20 aligned shielding in 3d assembly
    [Laird-BMI-S-208-F__AND__BMI-S-208-C.sldasm, S1PCB.sldasm, cape_and_beagle_assembly.SLDASM]
2016-12-20 revert rename
    [132322.sldasm, 416131160802.sldasm, 761606048.sldasm, 761608904.sldasm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]
2016-12-20 modify stick for push button
    [push_stick.SLDPRT, push_stick.STL, rocket_case_v1.STL]
2016-12-21 add acrylic cover plate (corrected with hole for button)
2016-12-21 rename hardware/case folder update relevant README files
    [132322.sldasm, 416131160802.sldasm, 761606048.sldasm, 761608904.sldasm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]
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2016-12-23 fixed 0.1mm distance error
    [rocket_case_v1.SLDPRT, rocket_case_v1.STL]
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2017-02-17 add calibration error calculation and writing log file, closes #93
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2017-02-27 Update testpoints to new version without solder paste, regenerate production outputs
    [Assembly Testpoint Report for PCB.csv, Cape.PrjPcb, PCB.GBL, PCB.GBO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]
2017-02-28 Fixed 32bit sample count bug
2017-04-19 fix beaglebone header ground loop (errata SUP-1), generate new output files
    [Assembly Testpoint Report for PCB.csv, Bill of Materials-Cape.xls, Cape.PrjPcb, PCB.GBL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]
2017-05-08 add RocketLogger Cape version 1.1. Fixes groud loop issue #97.
    [Bill of Materials-Cape.xls, PCB.GTS, PCB_Soldermask_Top.gbr]
2017-05-13 complete python file import (feature #98) - fix import of split files - fix channel merge - add getting absolute timestamps - add initial set of tests with sample data
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2017-06-30 update BME280 calibration, fix humidity channel sensor error handling and documentation
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2018-06-25 use fixed PRU sample data size, cleanup dynamic size dependent code
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2019-01-30 fix sample and remaining time calculation, fixes #121
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2019-05-06 fix calibration scales and plotting imports in tests
2019-05-06 add in-calibration error calculation and restructure calibration routine
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2019-05-15 move PRU data buffer back to DDR, revert default update rate to 1 Hz
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2019-06-14 fix status initialization and sharing, and calibration handling
2019-06-18 fix i2c device name, sensor error handling
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2019-06-26 fix sensor initialization
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2019-09-09 update image download to latest Debian buster 10.1 release, fix sensor status output
2019-09-26 fix calibration file check
2019-10-31 fix ambient sensor rate limiting
2020-01-31 revert reference timestamp update in calibration tests
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2020-04-26 fix dependencies and sdcard mount, more precise interrupt timestamp
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
